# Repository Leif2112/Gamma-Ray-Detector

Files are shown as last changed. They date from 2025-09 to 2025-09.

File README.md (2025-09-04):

# Gamma Ray Detector

Open-source SiPM + scintillator gamma-ray detector designed for CubeSat payloads and lab use. The project refines the Pi-Pico [Open Gamma Detector] into a higher-fidelity instrument with an upgraded TIA, low-noise photodiode bias, and temperature-compensated SiPM operation.

> **Project status:** electronics and simulations complete; prototype assembly and environmental testing outstanding.

## Project output
- **Space focus:** tailored for CubeSat constraints.  
- **Cleaner analogue front-end:** OPA355 TIA selected for faster slew and lower noise than OPA357.  
- **Stable SiPM bias:** LT3571-based photodiode bias supply with low ripple and temperature compensation strategy.  
- **Thermal robustness:** overvoltage held constant vs temperature to stabilise SiPM gain/PDE.

---

## High-level objectives

1. Develop a CubeSat-compatible system by enhancing the Pi-Pico DIY detector  
2. Build a working prototype  
3. Test detection performance and space suitability

## Architecture

- [visual diagram]

- [ ] [Visuals]

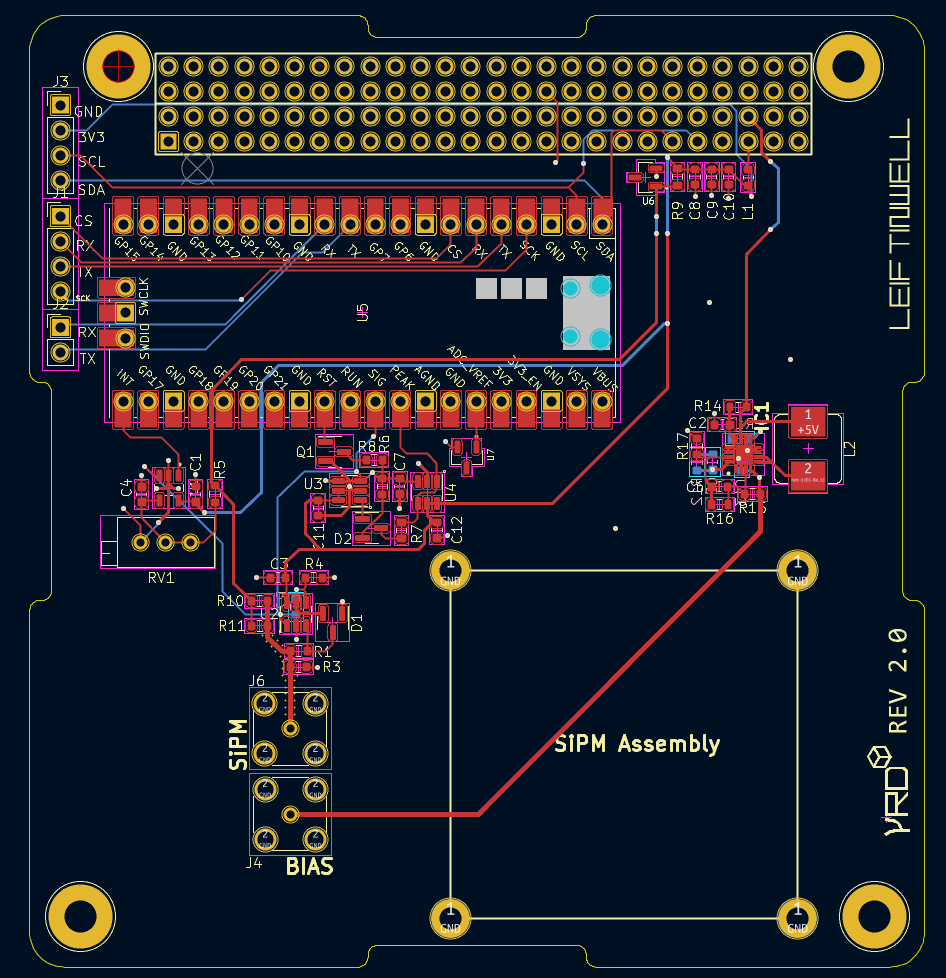
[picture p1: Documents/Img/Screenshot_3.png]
PCB V2 Readout


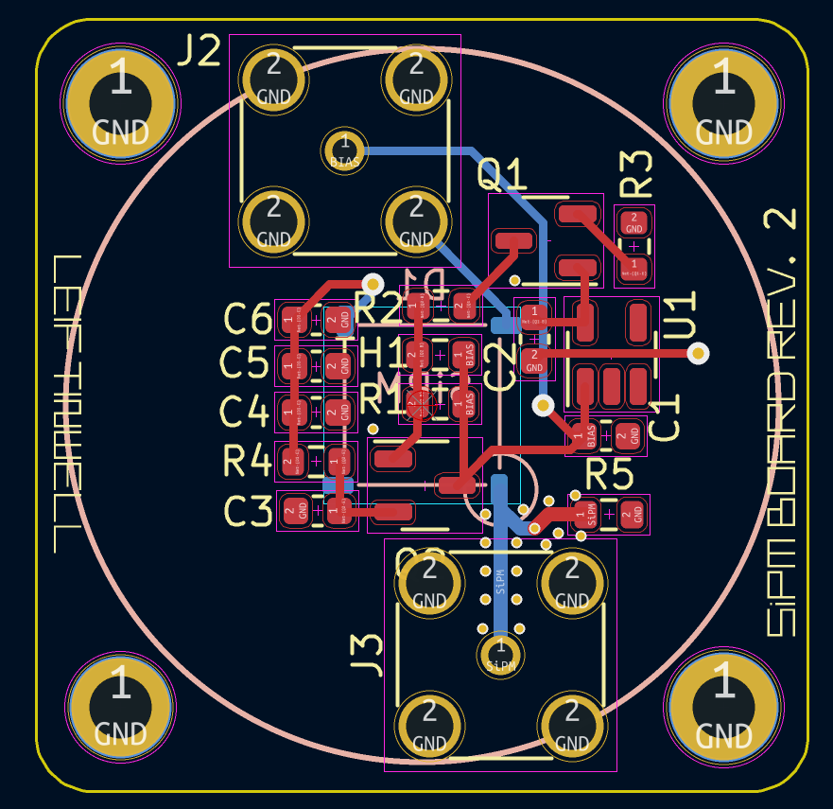
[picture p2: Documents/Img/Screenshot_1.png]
PCB V2 SiPM


## Features

- [ ] [Features list]

## Hardware

- [ ] [Hardware description]

## Firmware

- [ ] [Firmware dir.]

## Authors and acknowledgment

If you use this project in academic work, please cite the MSc thesis and this repository:
Tinwell, L. (2023). Gamma Ray Detector (MSc Thesis, University of Surrey).

***

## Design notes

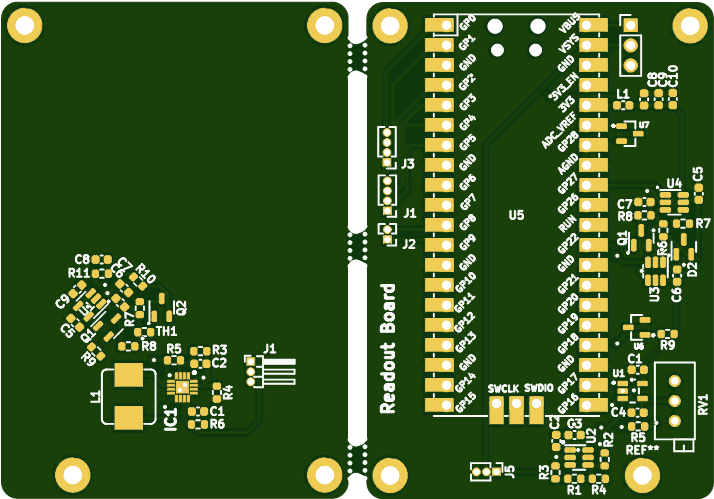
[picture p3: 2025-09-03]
Documents/Img/Untitled_Combined_Top.png

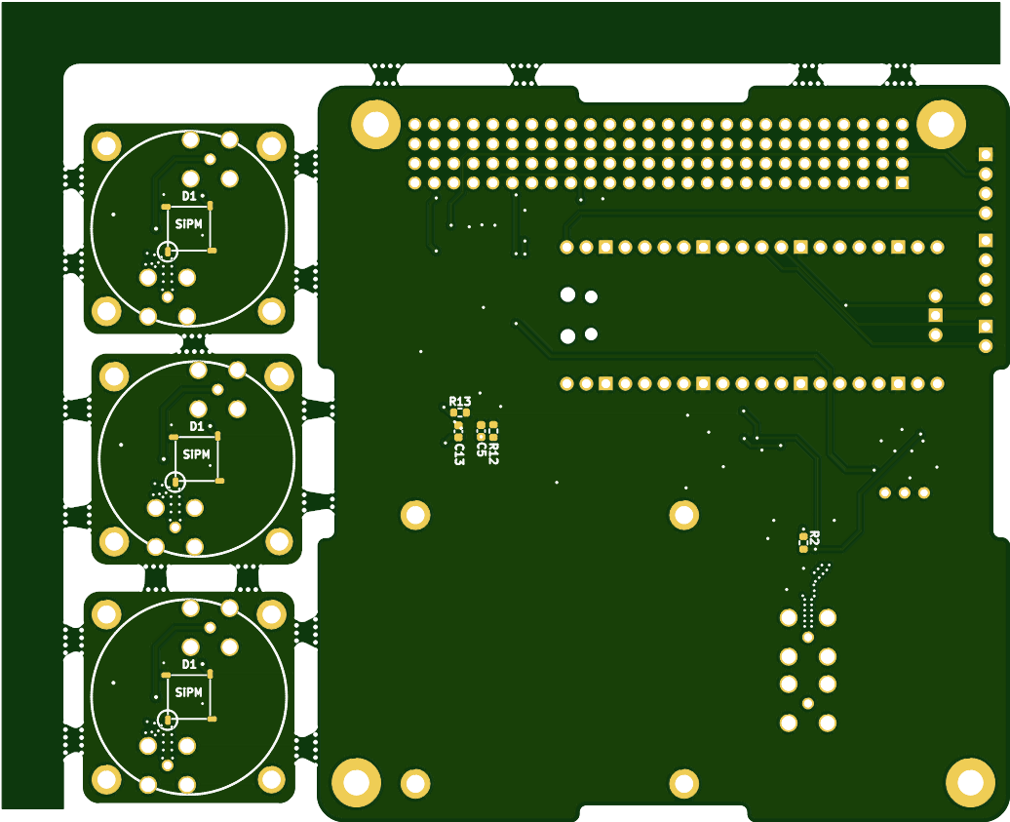
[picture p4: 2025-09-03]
Documents/Merged gerbers/Untitled_Combined_Bottom.png

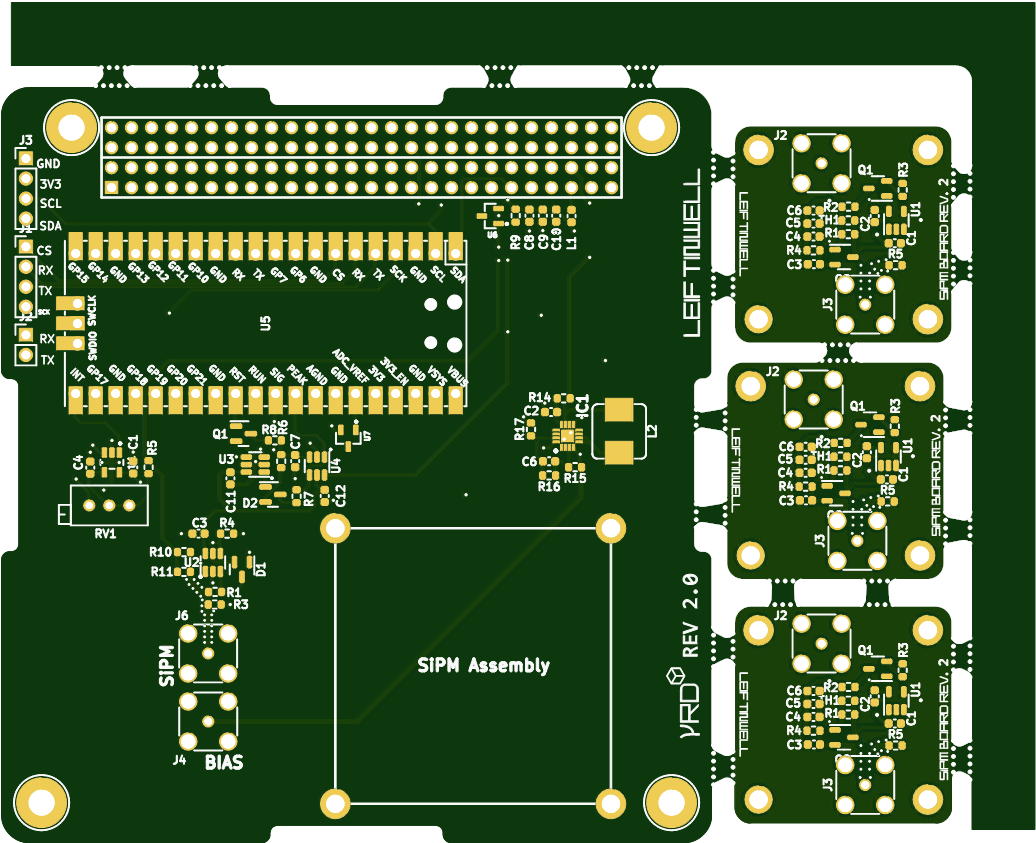
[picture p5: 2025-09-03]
Documents/Merged gerbers/Untitled_Combined_Top.png

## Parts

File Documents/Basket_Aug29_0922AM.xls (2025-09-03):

SHOPPING BASKET
This is not an invoice
29-Aug-23 09:22:22
 | Mouser No | Mfr. No | Manufacturer | Customer No | Description | RoHS | Lifecycle | Order Qty. | Price (GBP) | Ext.: (GBP)
1 | 187-CL10C100JB8NNNC | CL10C100JB8NNNC | Samsung Electro-Mechanics |  | Multilayer Ceramic Capacitors MLCC - SMD/SMT 10pF+/-5% 50V C0G 16 0603 | RoHS Compliant |  | 1 | £0.077 | £0.08
2 | 187-CL10B103KB8NNWC | CL10B103KB8NNWC | Samsung Electro-Mechanics |  | Multilayer Ceramic Capacitors MLCC - SMD/SMT 10nF+/-10% 50V X7R 1 0603 | RoHS Compliant |  | 2 | £0.077 | £0.15
3 | 187-CL10B104KB8NNNC | CL10B104KB8NNNC | Samsung Electro-Mechanics |  | Multilayer Ceramic Capacitors MLCC - SMD/SMT 100nF+/-10% 50V X7R 0603 | RoHS Compliant |  | 4 | £0.077 | £0.31
4 | 81-GRT188R61H225KE3D | GRT188R61H225KE13D | Murata |  | Multilayer Ceramic Capacitors MLCC - SMD/SMT 2.2 uF 50 VDC 10% 0603 X5R AEC-Q200 | RoHS Compliant |  | 2 | £0.255 | £0.51
5 | 863-MFC60035SMTTR | MICROFC-60035-SMT-TR | onsemi |  | Photodiodes C-SERIES 6MM 35U MLP | RoHS Compliant |  | 1 | £26.94 | £26.94
6 | 523-132134 | 132134 | Amphenol |  | RF Connectors / Coaxial Connectors SMA STRAIGHT PCB RECEPTACLE | RoHS Compliant By Exemption |  | 4 | £4.74 | £18.96
7 | 863-MMBT5088LT1G | MMBT5088LT1G | onsemi |  | Bipolar Transistors - BJT 50mA 35V NPN | RoHS Compliant |  | 2 | £0.147 | £0.29
8 | 71-CRCW0603-10-E3 | CRCW060310R0FKEA | Vishay |  | Thick Film Resistors - SMD 1/10watt 10ohms 1% | RoHS Compliant By Exemption |  | 1 | £0.077 | £0.08
9 | 71-CRCW060349R9FKEAC | CRCW060349R9FKEAC | Vishay |  | Thick Film Resistors - SMD 1/10Watt 49.9ohms 1% Commercial Use | RoHS Compliant By Exemption |  | 1 | £0.077 | £0.08
10 | 603-RT0603FRE0724KL | RT0603FRE0724KL | YAGEO |  | Thin Film Resistors - SMD 1/10W 24K ohm 1% 50p pm | RoHS Compliant By Exemption |  | 1 | £0.077 | £0.08
11 | 603-RT0603BRD0749K9L | RT0603BRD0749K9L | YAGEO |  | Thin Film Resistors - SMD 1/10W 49.9K ohm .1% 25ppm | RoHS Compliant By Exemption |  | 2 | £0.255 | £0.51
12 | 594-NTCS0603E3103FLT | NTCS0603E3103FLT | Vishay |  | NTC (Negative Temperature Coefficient) Thermistors 10Kohms 1% SMD | RoHS Compliant By Exemption |  | 1 | £0.609 | £0.61
13 | 595-TPS7B6950DBVR | TPS7B6950DBVR | Texas Instruments |  | LDO Voltage Regulators 150-mA, 40-V, low-IQ, low-dropout voltage regulator 5-SOT-23 -40 to 105 | RoHS Compliant |  | 1 | £0.648 | £0.65
14 | 667-ECH-U1C471JX5 | ECH-U1C471JX5 | Panasonic |  | Film Capacitors 470pF 16VDC 5% PPS FILM 0603 | RoHS Compliant |  | 1 | £0.417 | £0.42
15 | 810-CGA1A2X7R0J103MA | CGA1A2X7R0J103M030BA | TDK |  | Multilayer Ceramic Capacitors MLCC - SMD/SMT CGA 0201 6.3V 0.01uF X7R 20% AEC-Q200 | RoHS Compliant |  | 3 | £0.077 | £0.23
16 | 80-C0603C103K5REAUTO | C0603C103K5RECAUTO | KEMET |  | Multilayer Ceramic Capacitors MLCC - SMD/SMT 50V 0.01uF X7R 0603 10% AEC-Q200 | RoHS Compliant |  | 2 | £0.147 | £0.29
17 | 81-GRJ188R71H224KE1D | GRJ188R71H224KE11D | Murata |  | Multilayer Ceramic Capacitors MLCC - SMD/SMT 0.22 uF 50 VDC 10% 0603 X7R | RoHS Compliant |  | 1 | £0.185 | £0.19
18 | 80-C0603C105K8R | C0603C105K8RACTU | KEMET |  | Multilayer Ceramic Capacitors MLCC - SMD/SMT 10V 1uF X7R 0603 10% | RoHS Compliant |  | 1 | £0.077 | £0.08
19 | 187-CL10A106MQ8NNNC | CL10A106MQ8NNNC | Samsung Electro-Mechanics |  | Multilayer Ceramic Capacitors MLCC - SMD/SMT 10uF+/-20% 6.3V X5R 0603 | RoHS Compliant |  | 2 | £0.085 | £0.17
20 | 771-BAT54S-T/R | BAT54S,215 | Nexperia |  | Schottky Diodes & Rectifiers BAT54S/SOT23/TO-236AB | RoHS Compliant |  | 2 | £0.147 | £0.29
21 | 584-LT3571EUD#PBF | LT3571EUD#PBF | Analog Devices Inc. |  | Switching Voltage Regulators 75V DC/DC Conv for APD Bias | RoHS Compliant |  | 1 | £4.99 | £4.99
22 | 581-LMLP07B7M100DTAS | LMLP07B7M100DTAS | KYOCERA AVX |  | Power Inductors - SMD 10uH DCR= 101mOhm 20% 07B7 | RoHS Compliant |  | 1 | £0.725 | £0.73
23 | 81-BLM18KG102SN1D | BLM18KG102SN1D | Murata |  | Ferrite Beads 1000 OHM Alternate Sizing Guide Below | RoHS Compliant |  | 1 | £0.077 | £0.08
24 | 771-2N7002-T/R | 2N7002,215 | Nexperia |  | MOSFET 2N7002/SOT23/TO-236AB | RoHS Compliant |  | 1 | £0.224 | £0.22
25 | 603-RC0603FR-078R25L | RC0603FR-078R25L | YAGEO |  | Thick Film Resistors - SMD 8.25Ohms 1/10W 0603 1% | RoHS Compliant By Exemption |  | 1 | £0.077 | £0.08
26 | 756-GWCR0603-100RFT5 | GWCR0603-100RFT5 | TT Electronics |  | Thick Film Resistors - SMD 1/10W 100 Ohm 1% | RoHS Compliant |  | 2 | £0.108 | £0.22
27 | 603-SR0603FR-071KL | SR0603FR-071KL | YAGEO |  | Thick Film Resistors - SMD 1 kOhms 1/10 W 0603 1 % AEC-Q200 | RoHS Compliant By Exemption |  | 4 | £0.324 | £1.30
28 | 652-CR0603JW-202ELF | CR0603-JW-202ELF | Bourns |  | Thick Film Resistors - SMD 2K ohm 5% | RoHS Compliant By Exemption |  | 1 | £0.077 | £0.08
29 | 603-RV0603FR-0710KL | RV0603FR-0710KL | YAGEO |  | Thick Film Resistors - SMD 10 kOhms 100 mW 0603 1% | RoHS Compliant By Exemption |  | 2 | £0.185 | £0.37
30 | 603-RT0603FRE1320KL | RT0603FRE1320KL | YAGEO |  | Thin Film Resistors - SMD 1/10W 20K ohm 1% 50p pm | RoHS Compliant By Exemption |  | 1 | £0.077 | £0.08
31 | 603-RT0603FRE0726K1L | RT0603FRE0726K1L | YAGEO |  | Thin Film Resistors - SMD 1/10W 26.1K ohm 1% 5 0ppm | RoHS Compliant By Exemption |  | 1 | £0.077 | £0.08
32 | 603-RT0603FRE0729K4L | RT0603FRE0729K4L | YAGEO |  | Thin Film Resistors - SMD 1/10W 29.4K ohm 1% 5 0ppm | RoHS Compliant By Exemption |  | 1 | £0.077 | £0.08
33 | 71-CRCW0603-210K | CRCW0603210KFKTA | Vishay |  | Thick Film Resistors - SMD 1/10watt 210Kohms 1% | No |  | 3 | £0.154 | £0.46
34 | 603-RT0603FRD071ML | RT0603FRD071ML | YAGEO |  | Thin Film Resistors - SMD 1M ohm 1% 25 ppm High-Precision | RoHS Compliant By Exemption |  | 1 | £0.077 | £0.08
35 | 652-3296X-1-503 | 3296X-1-503 | Bourns |  | Trimmer Resistors - Through Hole 3/8" 50Kohms Sealed Horizontal Adjust | No |  | 1 | £3.42 | £3.42
36 | 700-LM4040AIM3-3.0T | LM4040AIM3-3.0+T | Analog Devices Inc. |  | Voltage References Improved Precision Micropower Shunt Voltage Reference with Multiple Reverse Breakdown Voltages | RoHS Compliant |  | 2 | £2.12 | £4.24
37 | 595-OPA355NA/250 | OPA355NA/250 | Texas Instruments |  | High Speed Operational Amplifiers 2.5V 200MHz GBW CMOS Sngl | RoHS Compliant |  | 3 | £1.75 | £5.25
38 | 595-TLV3201AIDBVR | TLV3201AIDBVR | Texas Instruments |  | Analog Comparators 40ns,micro-Pwr,RRI Sgl Channel Comp | RoHS Compliant |  | 1 | £1.12 | £1.12
By submitting your order you agree to these terms and conditions. (https://www.mouser.co.uk/saleterms) |  |  |  |  |  |  |  |  | Merchandise: | £73.80
Prices are reflected at the date and time shown. |  |  |  |  |  |  |  |  | Delivery Charge: | £0.00

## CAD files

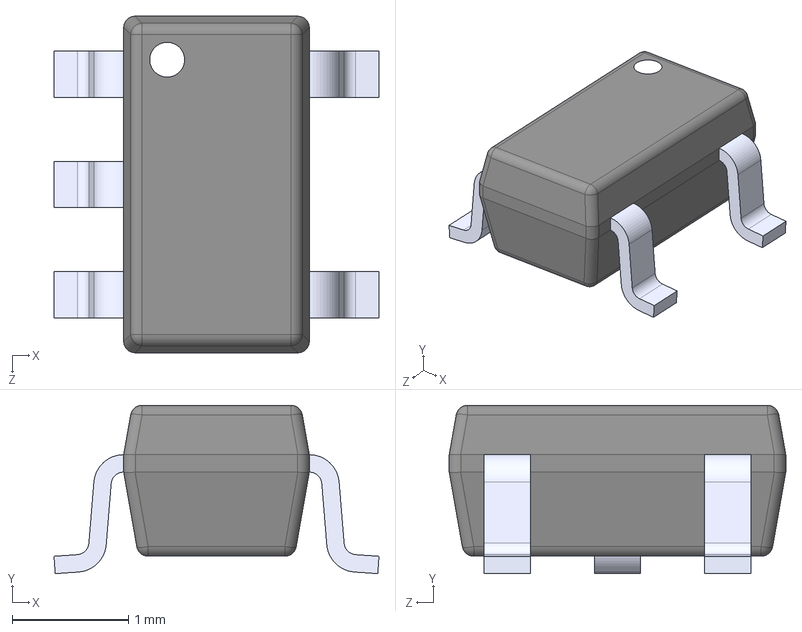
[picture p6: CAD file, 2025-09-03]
SiPM output/symlib/TLV3201AIDBVR.step
2.80 x 1.45 x 2.90 mm

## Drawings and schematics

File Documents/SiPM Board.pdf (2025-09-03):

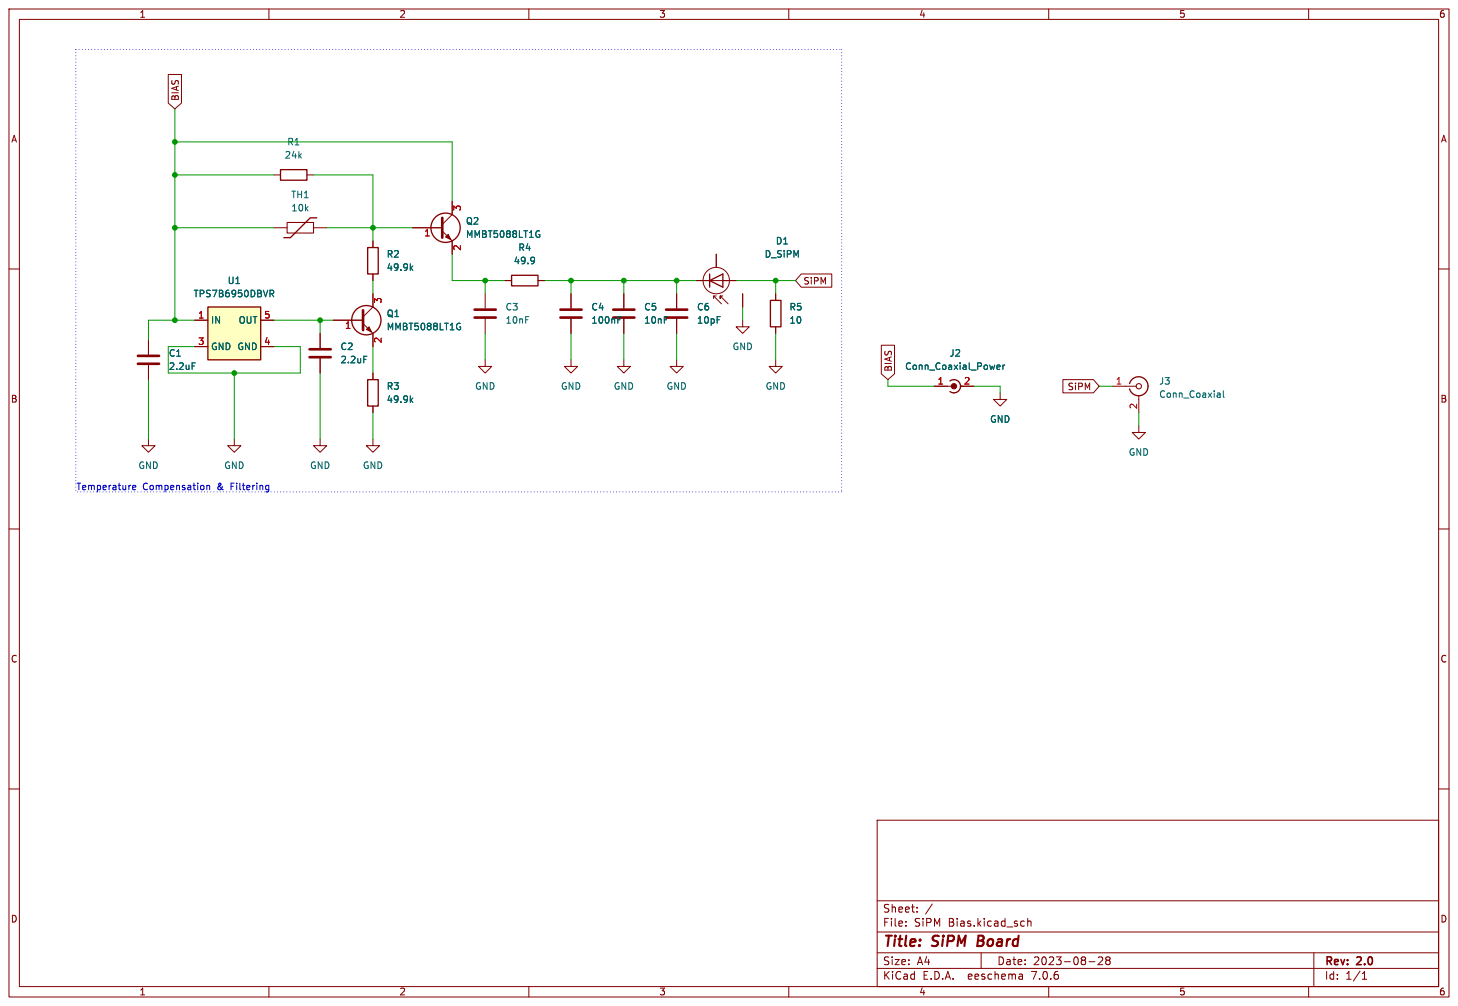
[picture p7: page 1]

Id: 1/1 Title: SiPM Board

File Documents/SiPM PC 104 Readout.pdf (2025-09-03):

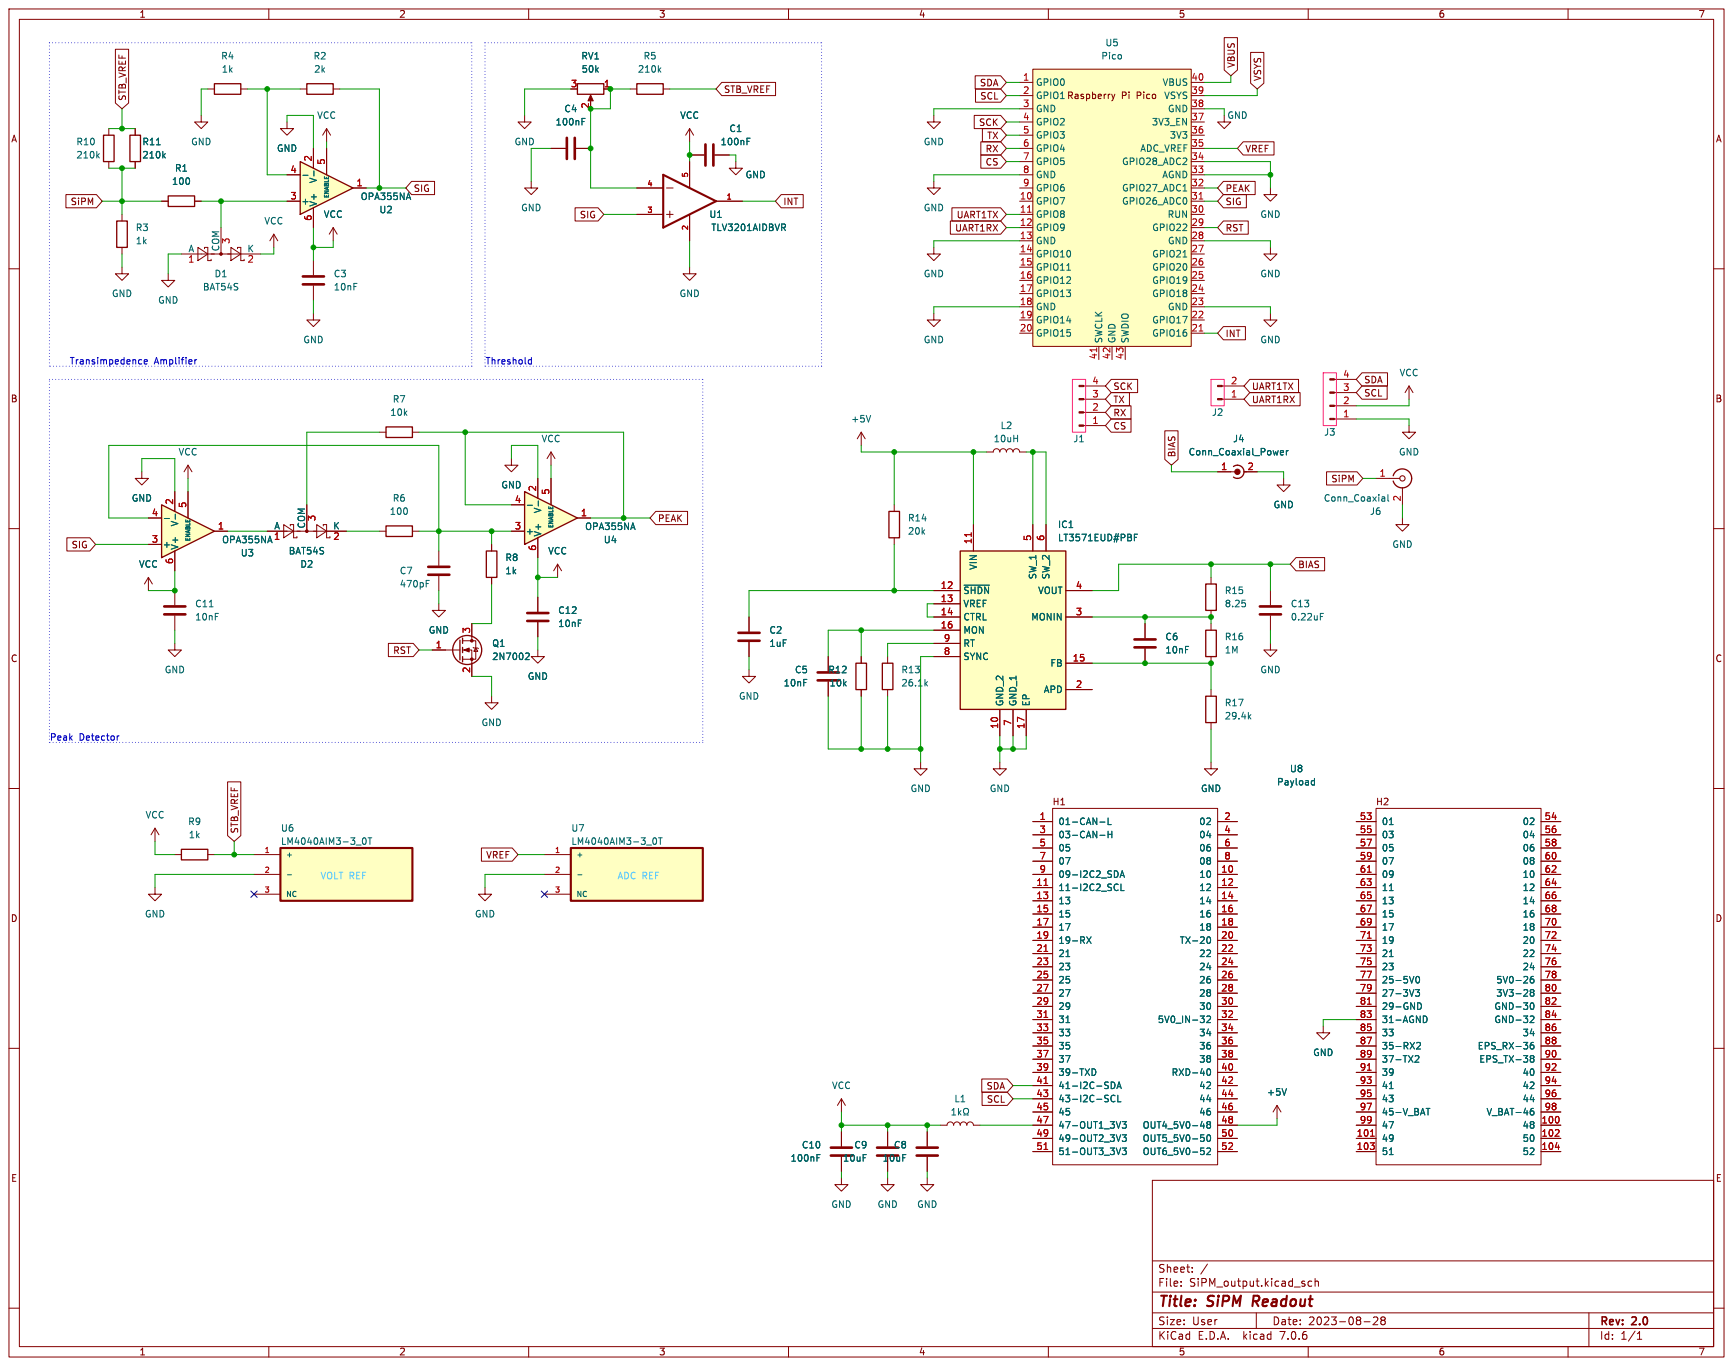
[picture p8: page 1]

Id: 1/1 Title: SiPM Readout File: SiPM_output.kicad_sch Sheet: /

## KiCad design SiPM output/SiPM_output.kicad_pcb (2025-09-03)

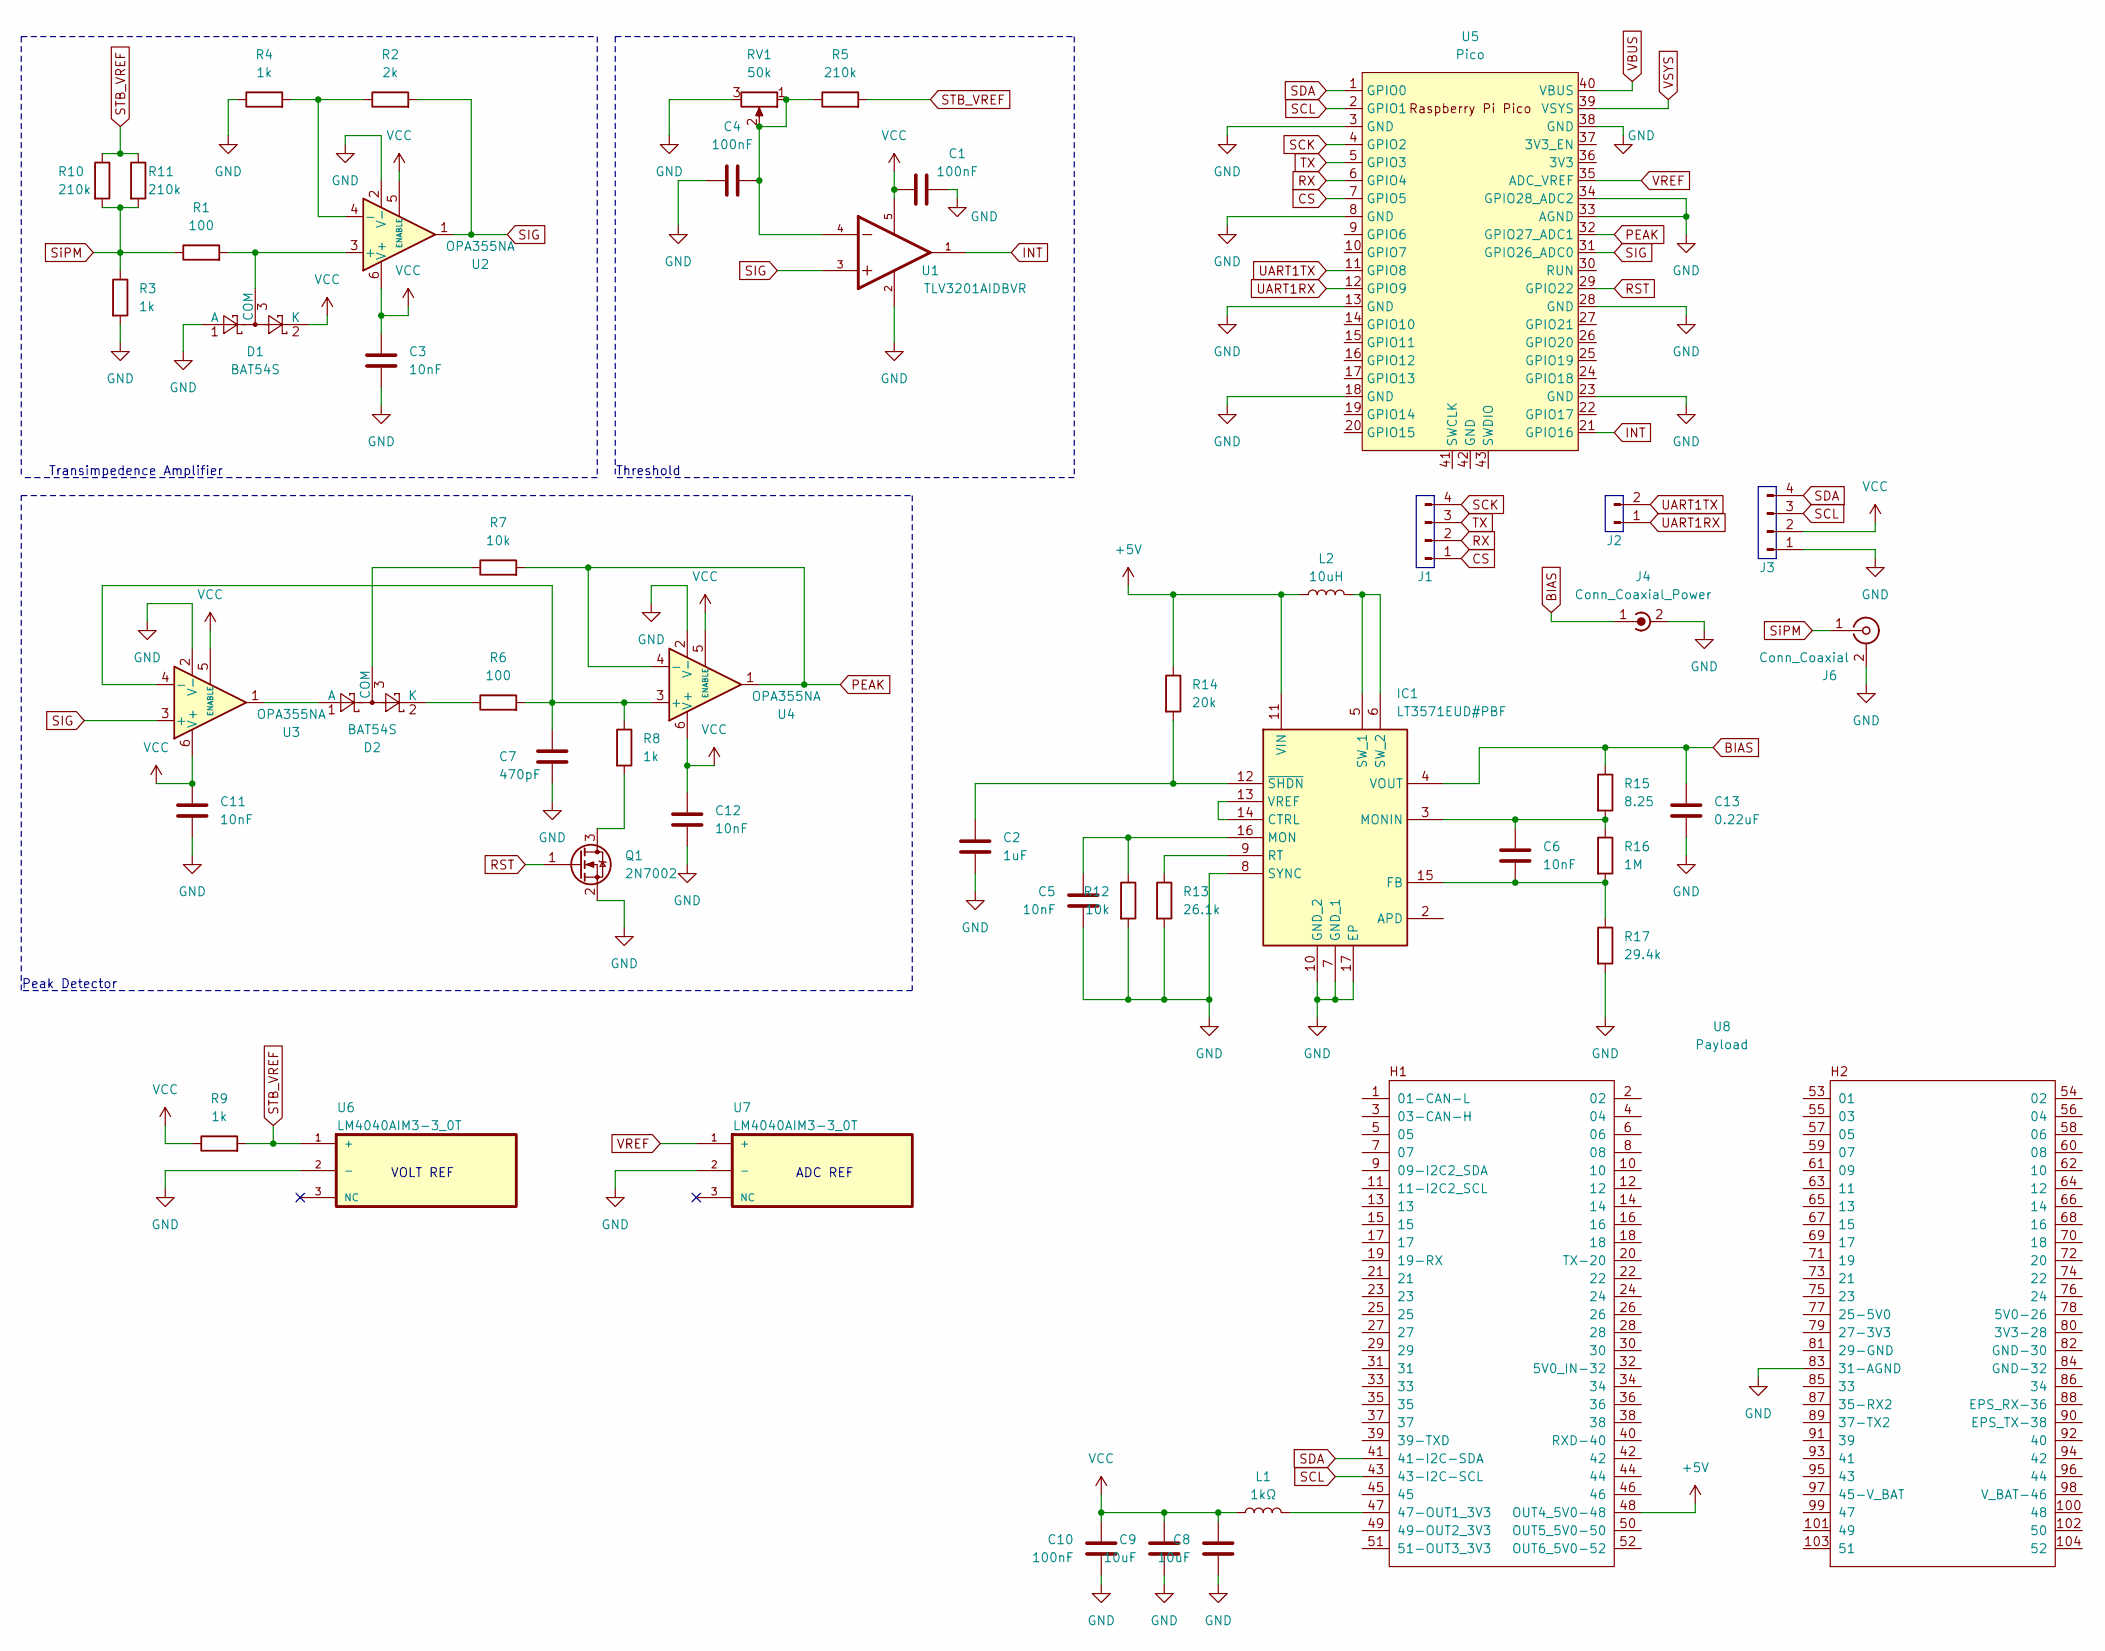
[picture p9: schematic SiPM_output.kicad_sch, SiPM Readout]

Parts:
C1, C4, C10: 100nF; C_0603_1608Metric
C2: 1uF; C_0603_1608Metric
C3, C5, C6, C11, C12: 10nF; C_0603_1608Metric
C7: 470pF; C_0603_1608Metric
C8, C9: 10uF; C_0603_1608Metric
C13: 0.22uF; C_0603_1608Metric
D1, D2: BAT54S; SOT-23
IC1: LT3571EUD#PBF; QFN50P300X300X80-17N-D
J1, J3: Conn_01x04_Pin; PinHeader_1x04_P2.54mm_Vertical
J2: Conn_01x02_Pin; PinHeader_1x02_P2.54mm_Vertical
J4: Conn_Coaxial_Power; SMA_Amphenol_132134-14_Vertical
J6: Conn_Coaxial; SMA_Amphenol_132134-14_Vertical
L1: 1kΩ; L_0603_1608Metric
L2: 10uH; L_Bourns_SRP7028A_7.3x6.6mm
Q1: 2N7002; SOT-23
R1, R6: 100; R_0603_1608Metric
R2: 2k; R_0603_1608Metric
R3, R4, R8, R9: 1k; R_0603_1608Metric
R5, R10, R11: 210k; R_0603_1608Metric
R7, R12: 10k; R_0603_1608Metric
R13: 26.1k; R_0603_1608Metric
R14: 20k; R_0603_1608Metric
R15: 8.25; R_0603_1608Metric
R16: 1M; R_0603_1608Metric
R17: 29.4k; R_0603_1608Metric
RV1: 50k; Potentiometer_Bourns_3296X_Horizontal
U1: TLV3201AIDBVR; SOT95P280X145-5N
U2, U3, U4: OPA355NA; SOT-23-6
U5: Pico; RPi_Pico_SMD_TH
U6, U7: LM4040AIM3-3_0T; SOT95P237X112-3N
U8: Payload; PC104-Standard

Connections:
+5V: IC1.11 (VIN), L2.1, R14.1, U8.48 (OUT4_5V0-48)
BIAS: C13.1, IC1.4 (VOUT), J4.1 (In), R15.1
CS: J1.1, U5.7 (GPIO5)
GND: C1.2, C2.2, C3.2, C4.1, C5.2, C7.2, C8.2, C9.2, C10.2, C11.2, C12.2, C13.2, D1.1 (A), IC1.7 (GND_1), IC1.8 (SYNC), IC1.10 (GND_2), IC1.17 (EP), J3.1, J4.2 (Ext), J6.2 (Ext), Q1.2 (S), R3.2, R4.1, R12.2, R13.2, R17.2, RV1.3, U1.2, U2.2 (V-), U3.2 (V-), U4.2 (V-), U5.3 (GND), U5.8 (GND), U5.13 (GND), U5.18 (GND), U5.23 (GND), U5.28 (GND), U5.33 (AGND), U5.34 (GPIO28_ADC2), U5.38 (GND), U6.2 (-), U7.2 (-), U8.83 (31-AGND)
INT: U1.1, U5.21 (GPIO16)
unnamed: C4.2, R5.1, RV1.1, RV1.2, U1.4
unnamed: D1.3 (COM), R1.2, U2.3 (+)
unnamed: D2.1 (A), U3.1
unnamed: D2.3 (COM), R7.1
unnamed: D2.2 (K), R6.1
unnamed: IC1.13 (VREF), IC1.14 (CTRL)
unnamed: C6.2, IC1.15 (FB), R16.2, R17.1
unnamed: C5.1, IC1.16 (MON), R12.1
unnamed: C6.1, IC1.3 (MONIN), R15.2, R16.1
unnamed: IC1.9 (RT), R13.1
unnamed: IC1.5 (SW_1), IC1.6 (SW_2), L2.2
unnamed: C2.1, IC1.12 (~SHDN), R14.2
unnamed: Q1.3 (D), R8.2
unnamed: R2.1, R4.2, U2.4 (-)
unnamed: C7.1, R6.2, R8.1, U3.4 (-), U4.3 (+)
unnamed: L1.1, U8.47 (47-OUT1_3V3)
PEAK: R7.2, U4.1, U4.4 (-), U5.32 (GPIO27_ADC1)
RST: Q1.1 (G), U5.29 (GPIO22)
RX: J1.2, U5.6 (GPIO4)
SCK: J1.4, U5.4 (GPIO2)
SCL: J3.3, U5.2 (GPIO1), U8.43 (43-I2C-SCL)
SDA: J3.4, U5.1 (GPIO0), U8.41 (41-I2C-SDA)
SIG: R2.2, U1.3, U2.1, U3.3 (+), U5.31 (GPIO26_ADC0)
STB_VREF: R5.2, R9.2, R10.1, R11.1, U6.1 (+)
SiPM: J6.1 (In), R1.1, R3.1, R10.2, R11.2
TX: J1.3, U5.5 (GPIO3)
UART1RX: J2.1, U5.12 (GPIO9)
UART1TX: J2.2, U5.11 (GPIO8)
VBUS: U5.40 (VBUS)
VCC: C1.1, C3.1, C8.1, C9.1, C10.1, C11.1, C12.1, D1.2 (K), J3.2, L1.2, R9.1, U1.5, U2.5 (ENABLE), U2.6 (V+), U3.5 (ENABLE), U3.6 (V+), U4.5 (ENABLE), U4.6 (V+)
VREF: U5.35 (ADC_VREF), U7.1 (+)
VSYS: U5.39 (VSYS)

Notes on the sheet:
Threshold
VOLT REF
Transimpedence Amplifier
Peak Detector
ADC REF

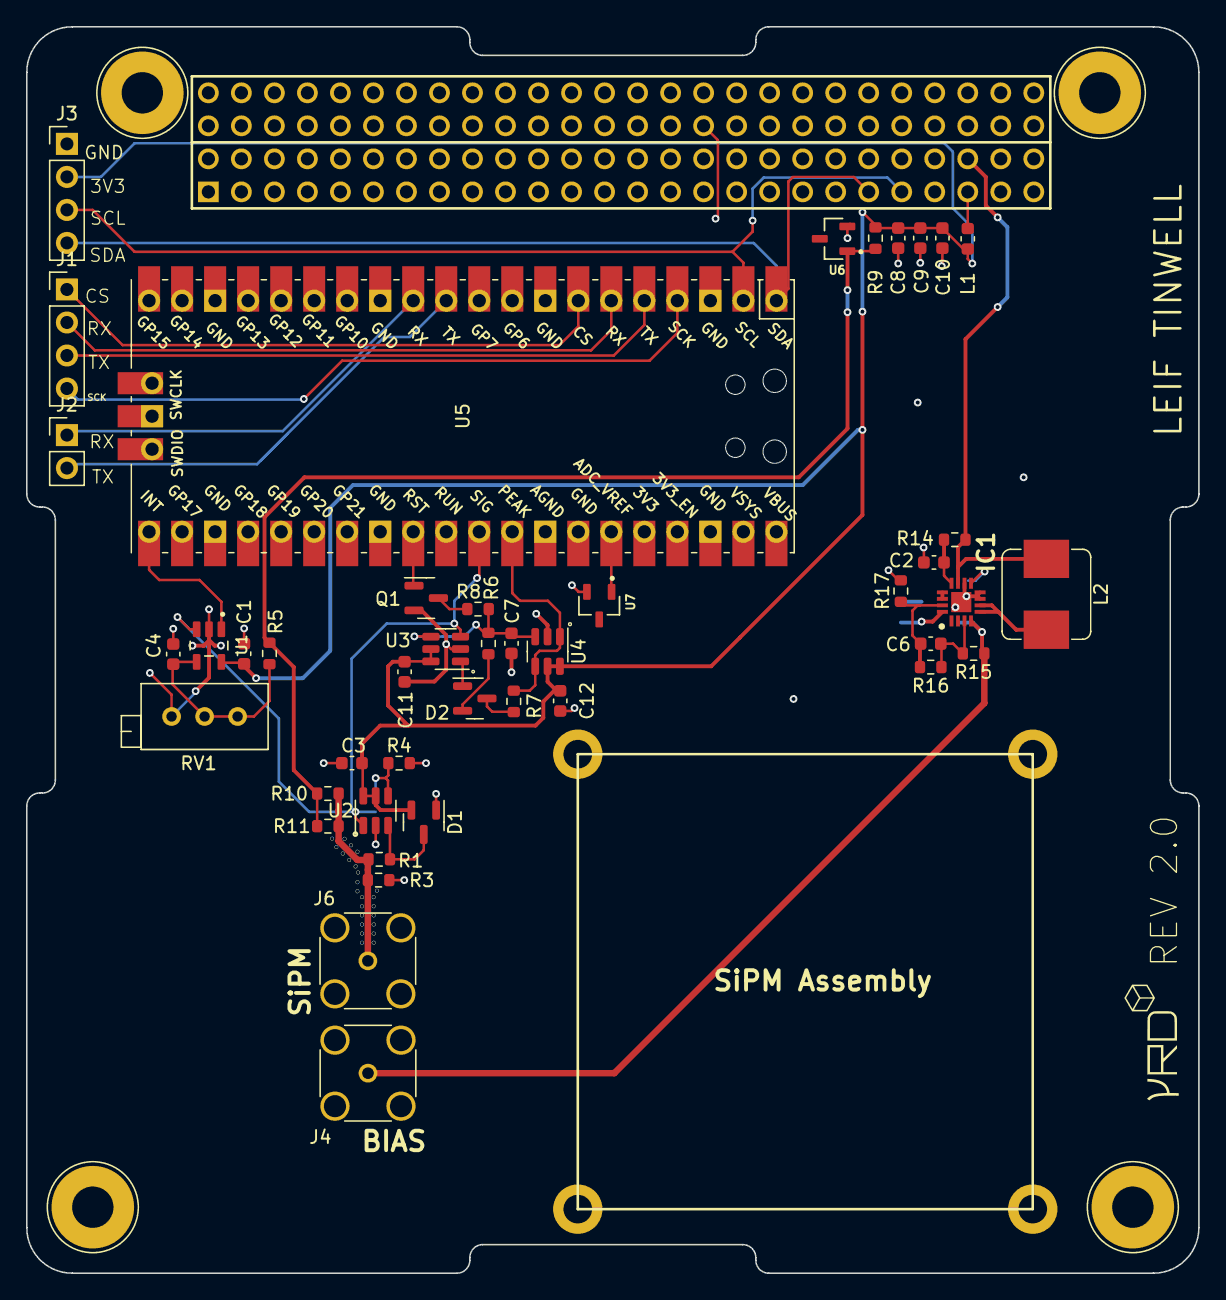
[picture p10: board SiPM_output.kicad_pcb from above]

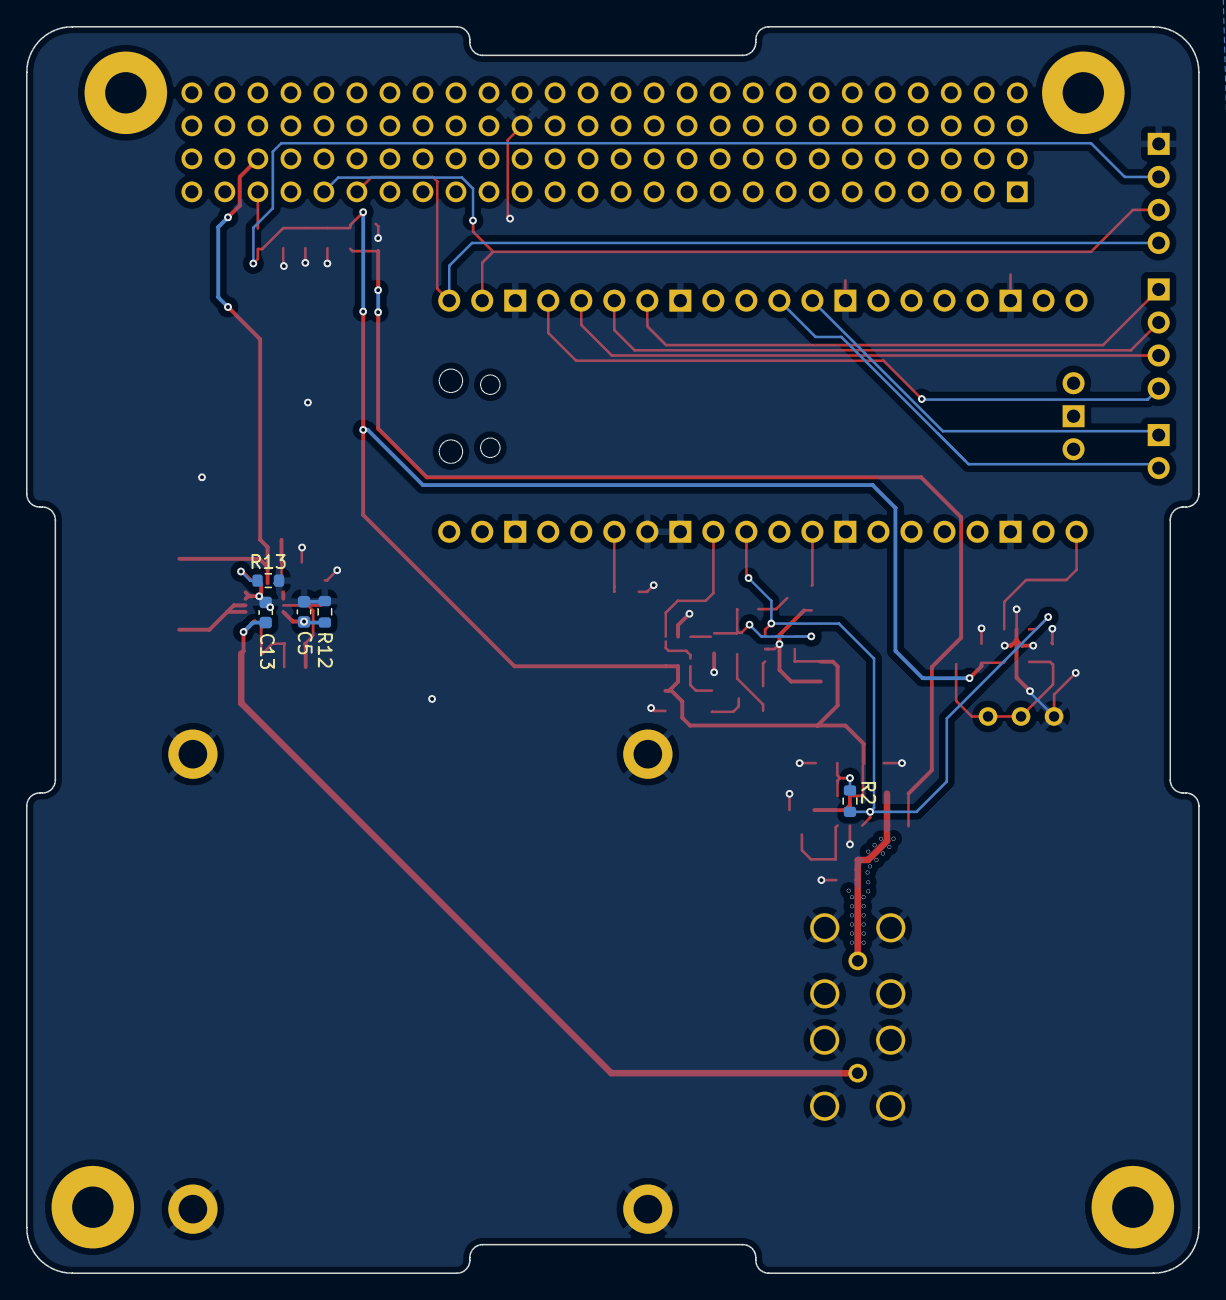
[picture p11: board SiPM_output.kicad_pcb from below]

Board: 2 copper layers, 90.2 x 95.9 mm, 50 parts (5 on the bottom side), 35 nets.

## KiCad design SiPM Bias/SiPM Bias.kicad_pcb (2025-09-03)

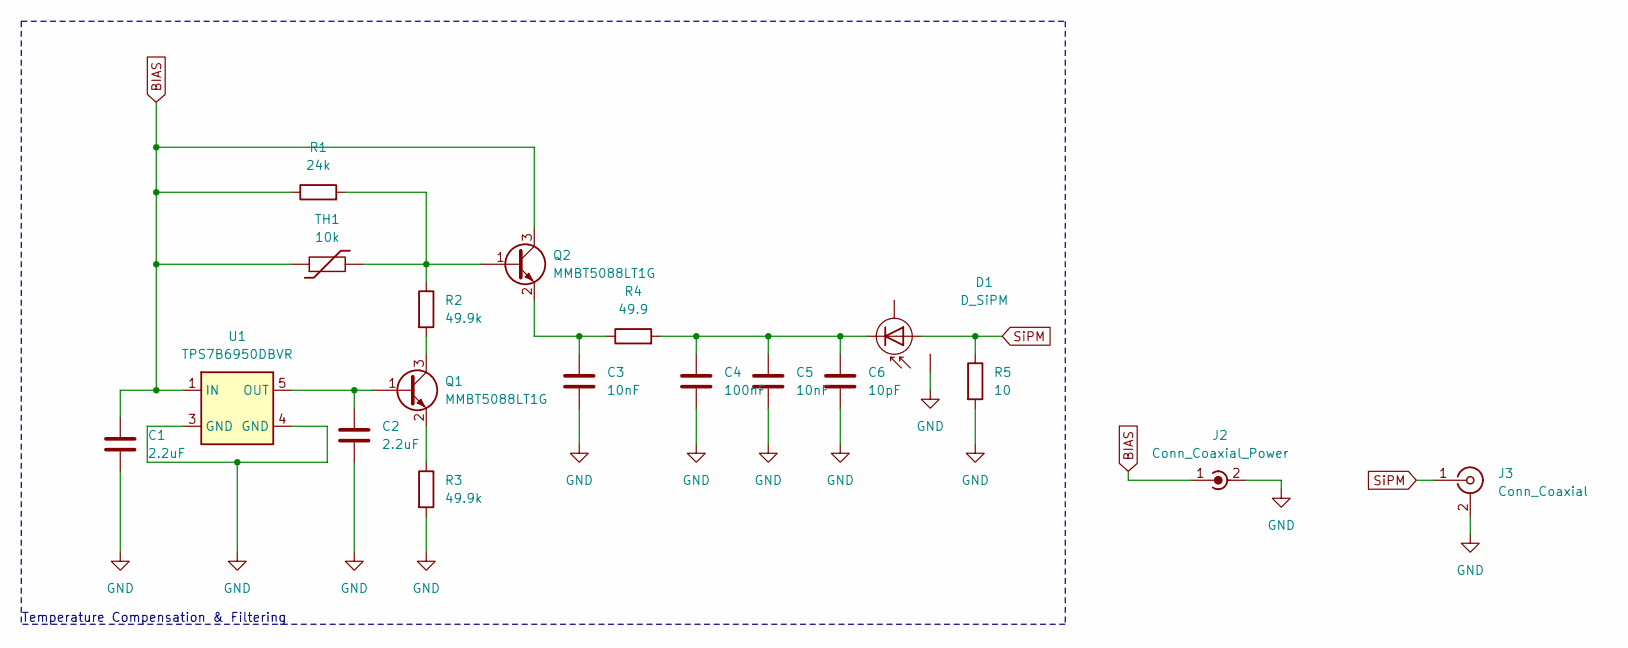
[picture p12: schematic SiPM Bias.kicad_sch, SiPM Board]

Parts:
C1, C2: 2.2uF; C_0603_1608Metric
C3, C5: 10nF; C_0603_1608Metric
C4: 100nF; C_0603_1608Metric
C6: 10pF; C_0603_1608Metric
D1: D_SiPM; MICROFC-60035
J2: Conn_Coaxial_Power; SMA_Amphenol_132134-14_Vertical
J3: Conn_Coaxial; SMA_Amphenol_132134-14_Vertical
Q1, Q2: MMBT5088LT1G; SOT-23-3
R1: 24k; R_0603_1608Metric
R2, R3: 49.9k; R_0603_1608Metric
R4: 49.9; R_0603_1608Metric
R5: 10; R_0603_1608Metric
TH1: 10k; R_0603_1608Metric
U1: TPS7B6950DBVR; SOT-23-5

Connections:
BIAS: C1.1, J2.1 (In), Q2.3 (C), R1.1, TH1.1, U1.1 (IN)
GND: C1.2, C2.2, C3.2, C4.2, C5.2, C6.2, D1.4 (G), J2.2 (Ext), J3.2 (Ext), R3.2, R5.2, U1.3 (GND), U1.4 (GND)
unnamed: C4.1, C5.1, C6.1, D1.3 (C), R4.2
unnamed: C2.1, Q1.1 (B), U1.5 (OUT)
unnamed: Q1.3 (C), R2.2
unnamed: Q1.2 (E), R3.1
unnamed: Q2.1 (B), R1.2, R2.1, TH1.2
unnamed: C3.1, Q2.2 (E), R4.1
SiPM: D1.1 (A), J3.1 (In), R5.1

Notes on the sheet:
Temperature Compensation & Filtering

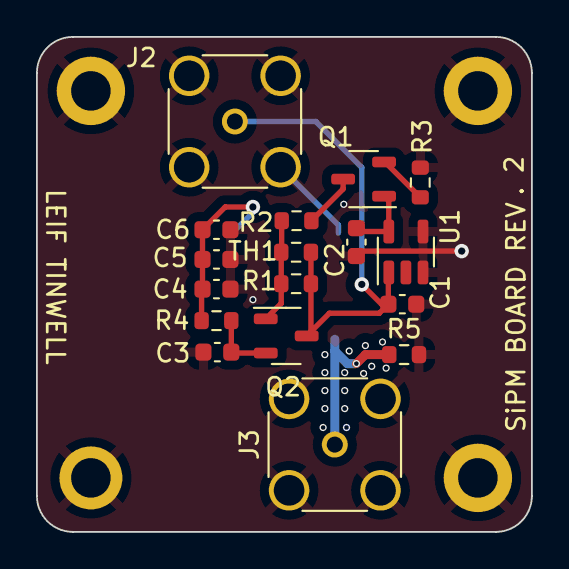
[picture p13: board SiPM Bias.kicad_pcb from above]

Board: 2 copper layers, 27.5 x 27.5 mm, 18 parts (1 on the bottom side), 9 nets.

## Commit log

2025-09-03 initialise repo and upload /documents
    [Basket_Aug29_0922AM.xls, combined.drl, combined.gbl, combined.gbo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]
2025-09-03 Upload SiPM Bias
    [SiPM Bias-B_Cu.gbl, SiPM Bias-B_Mask.gbs, SiPM Bias-B_Paste.gbp, SiPM Bias-B_Silkscreen.gbo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]
2025-09-03 Upload SiPM output
    [SiPM_output-B_Cu.gbl, SiPM_output-B_Mask.gbs, SiPM_output-B_Paste.gbp, SiPM_output-B_Silkscreen.gbo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]
